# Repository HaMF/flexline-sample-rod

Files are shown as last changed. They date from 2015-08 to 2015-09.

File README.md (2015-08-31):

# Flexline sample rod

This sample rod was designed to allow magnetic resonance experiments and simulateneous measurements in a Bruker flexline MD5 resonator hold inside of a Oxford CF395 flow cryostat. Included are 3d-models, drawings, PCB layouts and production recommendations as well as part lists of stock ISO KF parts.

All in all the holder works quite nicely. It positions the sample quite accurately in the cavity's center, is leak tight, does not show performance degradation or extraordinary large heat conductions at low temperatures (liquid Helium). Empty cavity measurements vs. sample holder in cavity measurements have been performed and will be added here for reference when the results are polished. A gear can be fitted to the top rod and the whole rod can be rotated automatically (http://hannes.maier-flaig.de/goniometer/)

**Please note:** Initial design documents were in German and some elements will probably have slipped through when translating to english (read: _all_ drawings). Units are exclusively metric. 
**Licence:** The holder design is licensed under the CERN Open Hardware License v1.2. 3D models of of-shelf ISO-KF flange parts (as available from the vendors web site) are included in the project and do not fall under the license (CERN OHL v1.2) of the whole project. Copyright as far as applicable remains with the manufacturer (see below).

## Pictures and performance

The full construction as autodesk project can be found in the subfolder ./1-autodesk project/ . Drawings are also exported
to PDF in the ./2-drawings folder. Here follows a description of the parts and description of the PCB holders:

### Top
Standard ISO-KF flanges are used. Conical reduction piece [Fig. ... (2)] is beneficial because it has more space to fit the connector.
Connecting the DC lines to a breakout box is performed using lemo connectors.

### V2A rod
To the lower KF16 KF a V2A rod is welded (i.e. hard soldered).

### Sample holder support
The sample rod is designed so that Bruker holder for standard quartz glass sample tubes also fit.
In this case an extension [Fig. ... (1)] has to be used that fits the plug of the DC lines.

Shown in [Fig. ... (2) and Fig ...] is the sample holder support for PCB sample holders.

## PCB sample holders
The PCB design in ./3-PCB/PCB.brd and ./3-PCB/PCB.pdf includes three layers: Dimensions, Holes, and Top (Copper)).
It was produced on FR4 IT158 (Tg155) 1mm thickness with a cooper only plating of 35µm. All of that is pretty standard
With the supplier "Hofmann Leiterplatten" production was fast and troublefree. After tax cost was roughly 190€ per 50pcs.

 + Soldering PCBs using a hotplate and soldering paste works quite nicely. Trim pins that stick out to the backside first.
 + When breaking PCB free from full plate, length dimensions are slightly too long thus the PCBs need to be shortened. (See below)

## Empty cavity vs loaded cavity measurements

Will follow.

# Part list

| Part # | Manufacturer          | Model               | Description                                                                        |
|--------|-----------------------|---------------------|------------------------------------------------------------------------------------|
| 1      | Lemo                  | HGP.1S.306.CLLSV    | 6-pin vacuum tight receptangle                                                     |
| 2      | Pfeiffer Vacuum       |                     | ISO KF-40 blind flange (Al)                                                        |
| 3      | Pfeiffer Vacuum       |                     | ISO KF-40 centering ring and o-ring                                                |
| 4      | Pfeiffer Vacuum       |                     | ISO KF-40-16 conical reduction (Al)                                                |
| 5      | Pfeiffer Vacuum       |                     | ISO KF-16 centering ring and o-ring                                                |
| 6      | Pfeiffer Vacuum       |                     | ISO KF-16 blind flange (Al)                                                        |
| 7      |                       |                     | V2A tube, 8mm OD, 7mm ID                                                           |
| 8      |                       |                     | PEEK-1000 rod, 10mm OD                                                             |
| 9      | W+P Products          | 605-006-1-2-00      | Plug 1.27mm grid, 2 rows each 3 pins at Conrad electronics: 739179-05              |
| 10     | W+P Products          | 712-1-006-2-10-00   | Plug 1.27mm grid, 2 rows each 3 pins, right angle at Conrad electronics: 718818-05 |
| 11     | Hofmann Leiterplatten |                     | PCB sample holder, see below                                                       |
| 12     | Lemo                  | 060080              | Cable for in-road as well as to breakout box                                       |
| 13     | Lemo                  | FFA.1S.306.CLAC52ZN | Plug, straight for breakout box. 2 times                                           |
| 14     | Lemo                  | ERA.1S.306.CLL      | Receptangle for breakout box                                                       |
| 15     | Telegärtner           | J01001A0043         | Isolating BNC female, straight for breakout box                                    |

## Remarks on parts, design considerations
 +  Sample side plug and jack are not polarity proof. This would be possible e.g. with Omnetics miniature plugs. 
    These are, however too expensive for this type of application and are not justified by just being polarity proof

# Further plans (and decisions that turned out not to be so clever)

 + Even though there are 6 DC lines, the PCBs connect only 5 into the cavity. Six leads would fit on the PCB just as well. 
   In case very low loading of the cavity is needed, only two leads should be used in any case.
 + PCB with 1.27x2.54mm² grid dimensions use 1.27x1.27mm² in next iterations. Rod-side is already the later gridsize.
 + PCB tolerance when breaking free instead of milling has been choosen too small. PCBs should be 0.5mm shorter in next iteration

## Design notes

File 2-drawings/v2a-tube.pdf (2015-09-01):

1

A4

Probenstab

## Edelstahl

Status | |nderungen | DATUM | Name

Gezeichnet

Kontrolliert

Norm

DATUM | Name
04.09.2014 | Hannes Maier-Flaig

4

4

0,0

0

P8,00 | P7,00 DURCH M7x0.5 - 6H
| INSIDE THREAD; min. 12 deep

Weld/Hard solder to KF16 Blindflansch

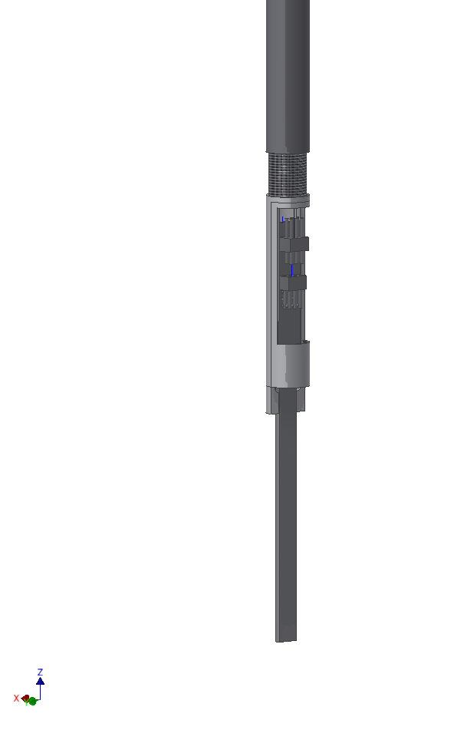
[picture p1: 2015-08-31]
0-images/bottom-pcb-holder.png

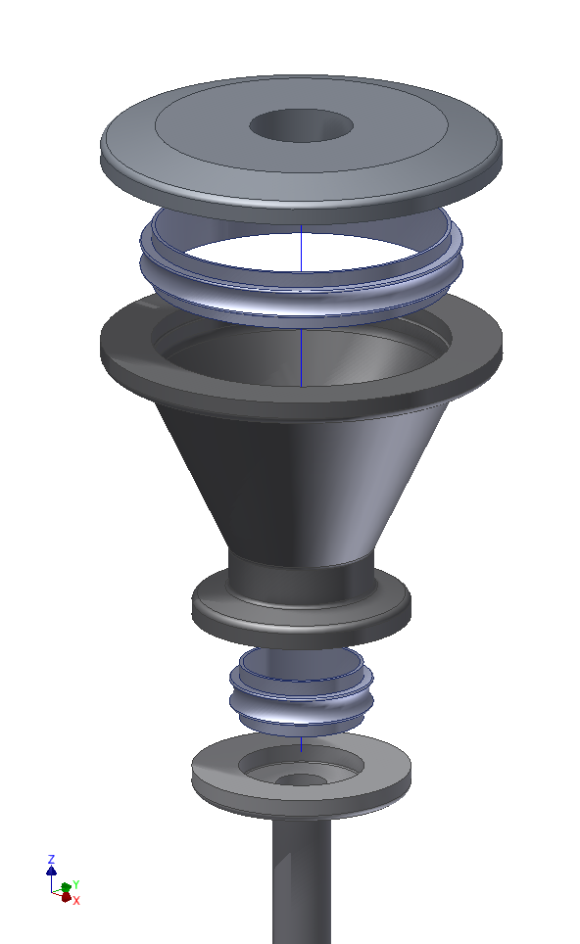
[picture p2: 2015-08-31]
0-images/top-flanges.png

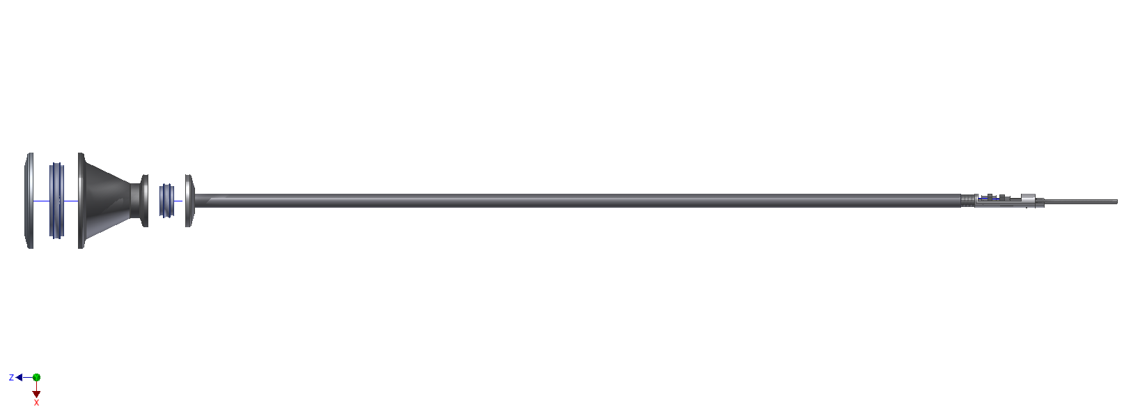
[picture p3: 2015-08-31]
0-images/total.png

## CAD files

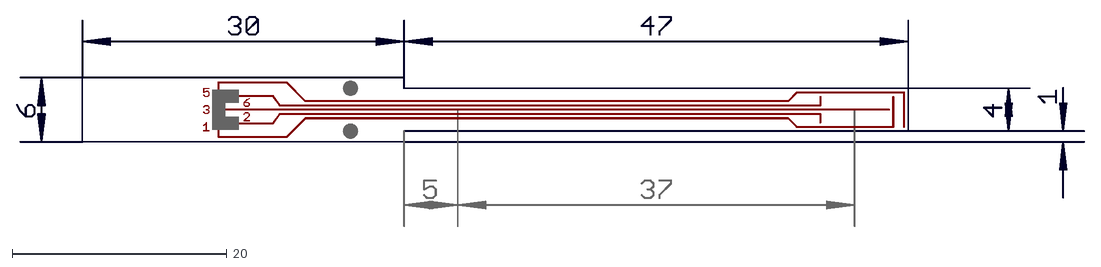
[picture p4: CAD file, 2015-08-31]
3-PCBs/PCB.dxf
99.6 x 19.6

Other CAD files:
1-autodesk project/drawings/PEEK-extension.dwg
1-autodesk project/drawings/KF16BF.dwg
1-autodesk project/drawings/KF40BF.dwg
1-autodesk project/drawings/v2a-tube.dwg
1-autodesk project/Importierte Komponenten/110FBL016/110FBL016.ipt
1-autodesk project/Importierte Komponenten/110FBL016/OldVersions/110FBL016.0002.ipt
1-autodesk project/Importierte Komponenten/110FBL016/OldVersions/110FBL016.0003.ipt
1-autodesk project/Importierte Komponenten/110FBL040/110FBL040.ipt
1-autodesk project/Importierte Komponenten/110FBL040/OldVersions/110FBL040.0001.ipt
1-autodesk project/Importierte Komponenten/110FBL040/OldVersions/110FBL040.0004.ipt
1-autodesk project/Importierte Komponenten/116ZRG016/116ZRG016.ipt
1-autodesk project/Importierte Komponenten/116ZRG016/OldVersions/116ZRG016.0002.ipt
1-autodesk project/Importierte Komponenten/116ZRG040/116ZRG040.ipt
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

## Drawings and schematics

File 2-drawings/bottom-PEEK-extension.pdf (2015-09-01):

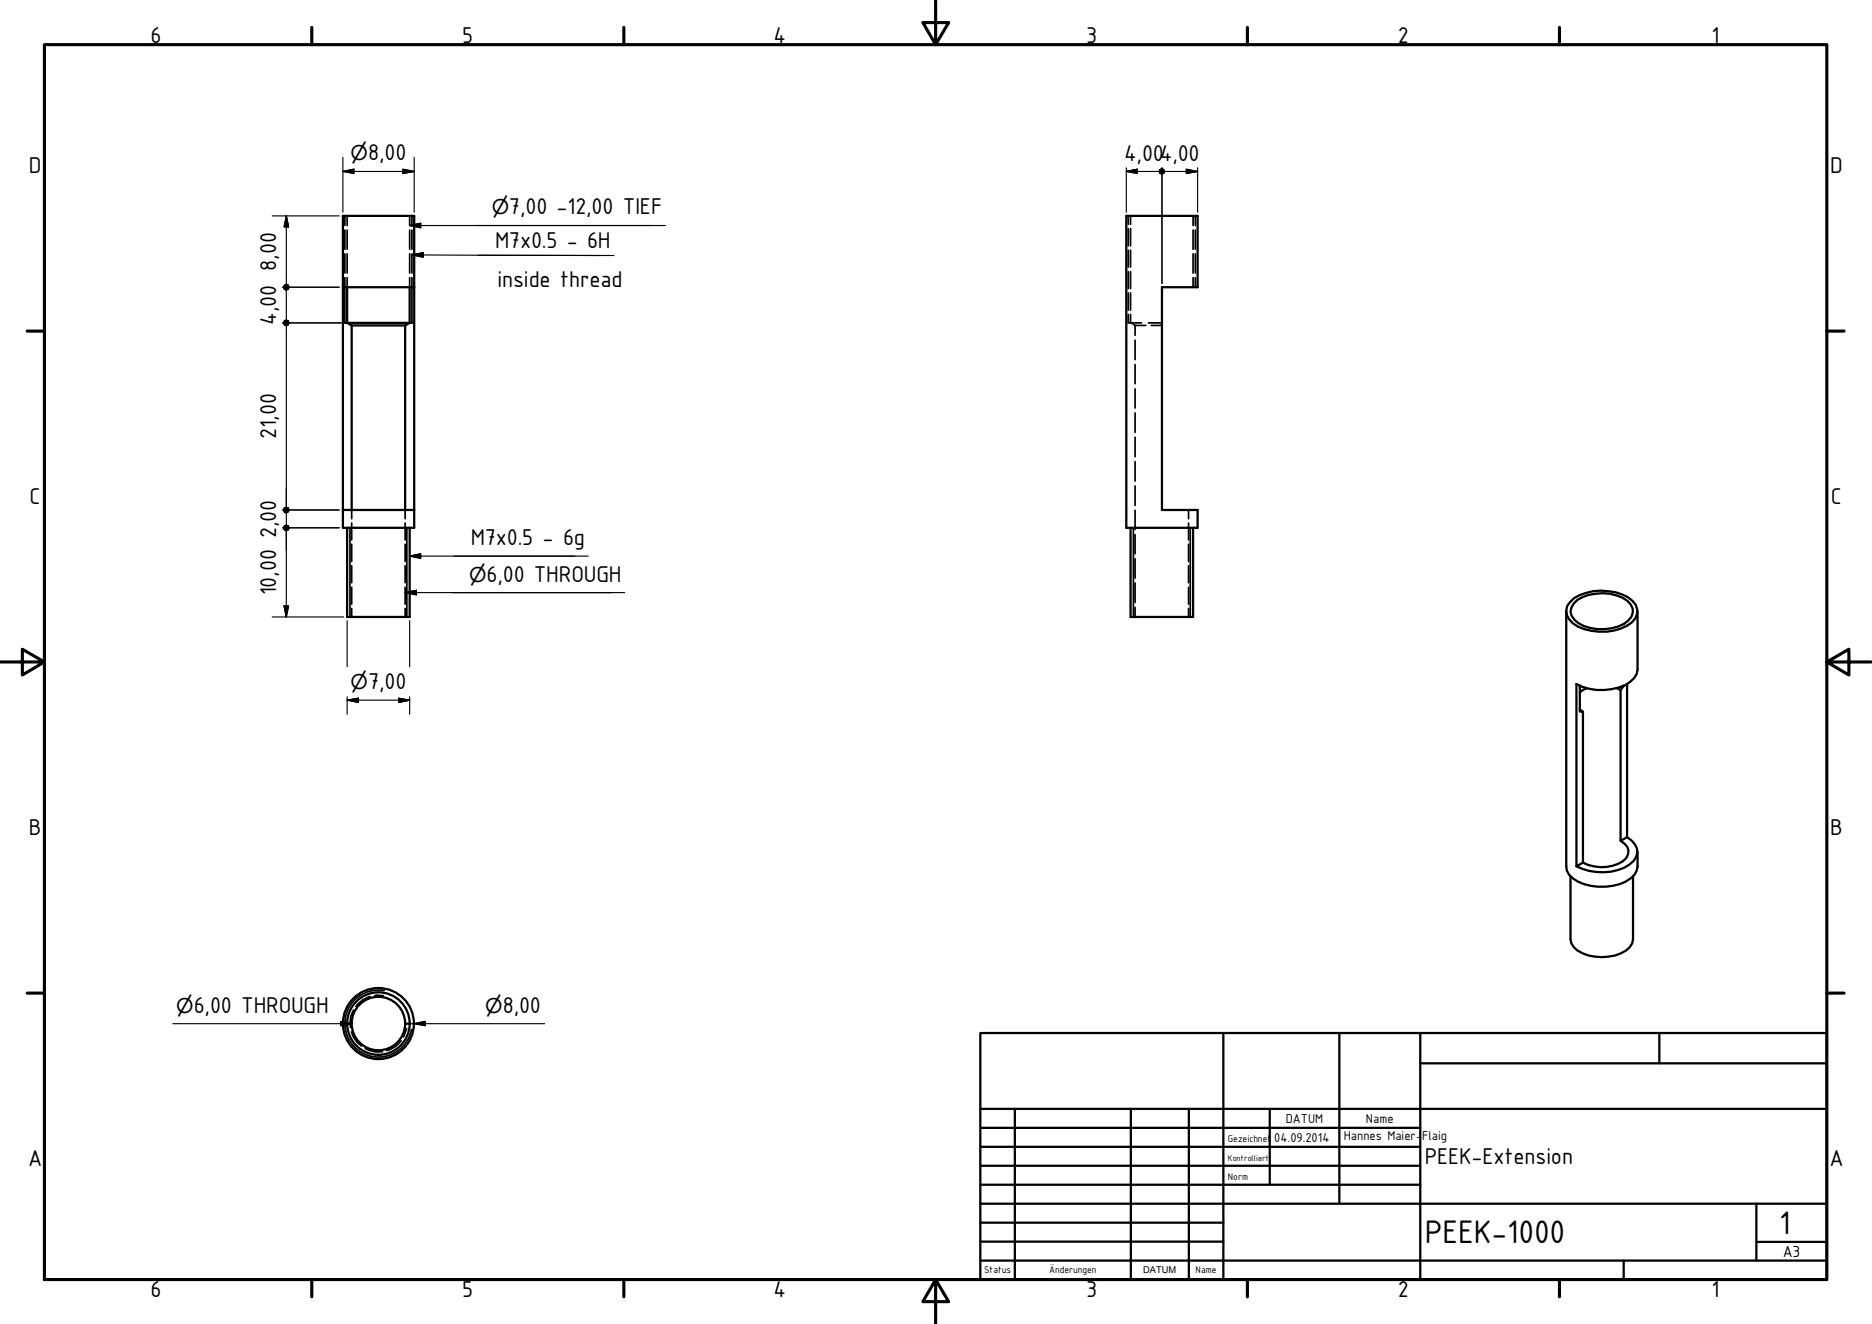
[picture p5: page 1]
PEEK-Extension; PEEK-1000; Status; |nderungen; DATUM; Name; Gezeichnet; Kontrolliert; Norm; Hannes Maier-Flaig; M7x0.5 - 6g P6,00 THROUGH; P7,00 -12,00 TIEF; P6,00 THROUGH; inside thread

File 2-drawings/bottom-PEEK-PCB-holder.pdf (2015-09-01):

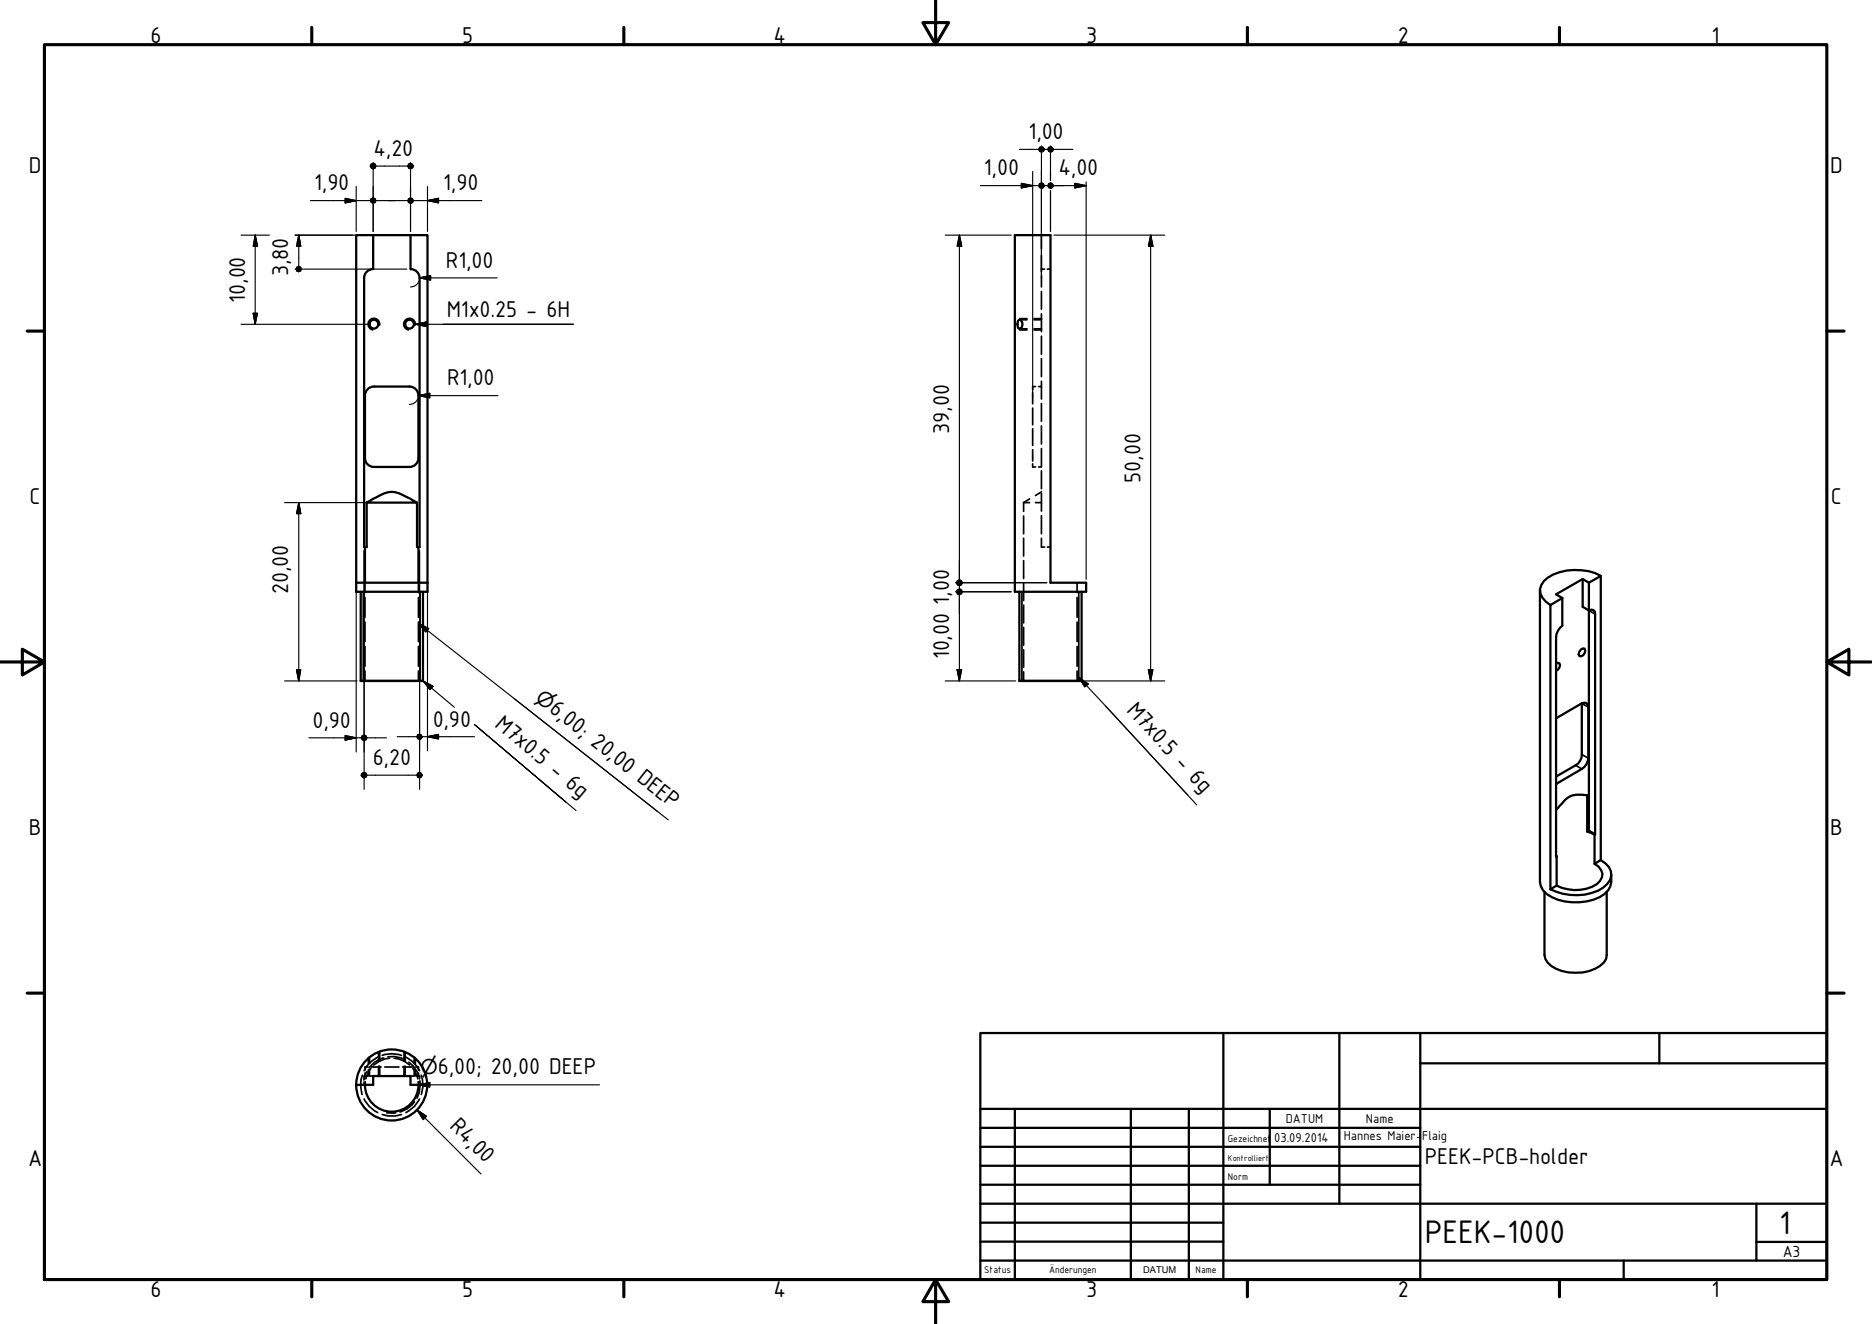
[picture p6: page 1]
PEEK-1000; Status; |nderungen; DATUM; Name; Gezeichnet; Kontrolliert; Norm; Hannes Maier-Flaig; P6,00; 20,00 DEEP

PEEK-PCB-holder

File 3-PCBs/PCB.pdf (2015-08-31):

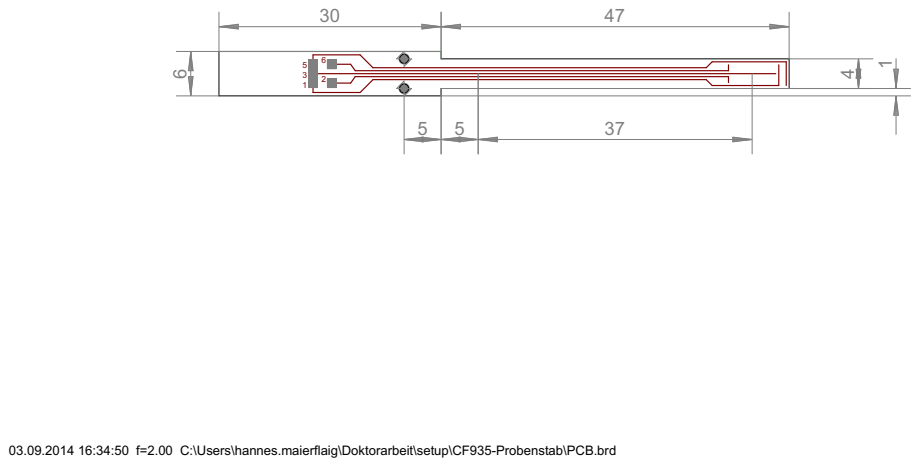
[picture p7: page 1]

03.09.2014 16:34:50 f=2.00 C:\Users\hannes.maierflaig\Doktorarbeit\setup\CF935-Probenstab\PCB.brd

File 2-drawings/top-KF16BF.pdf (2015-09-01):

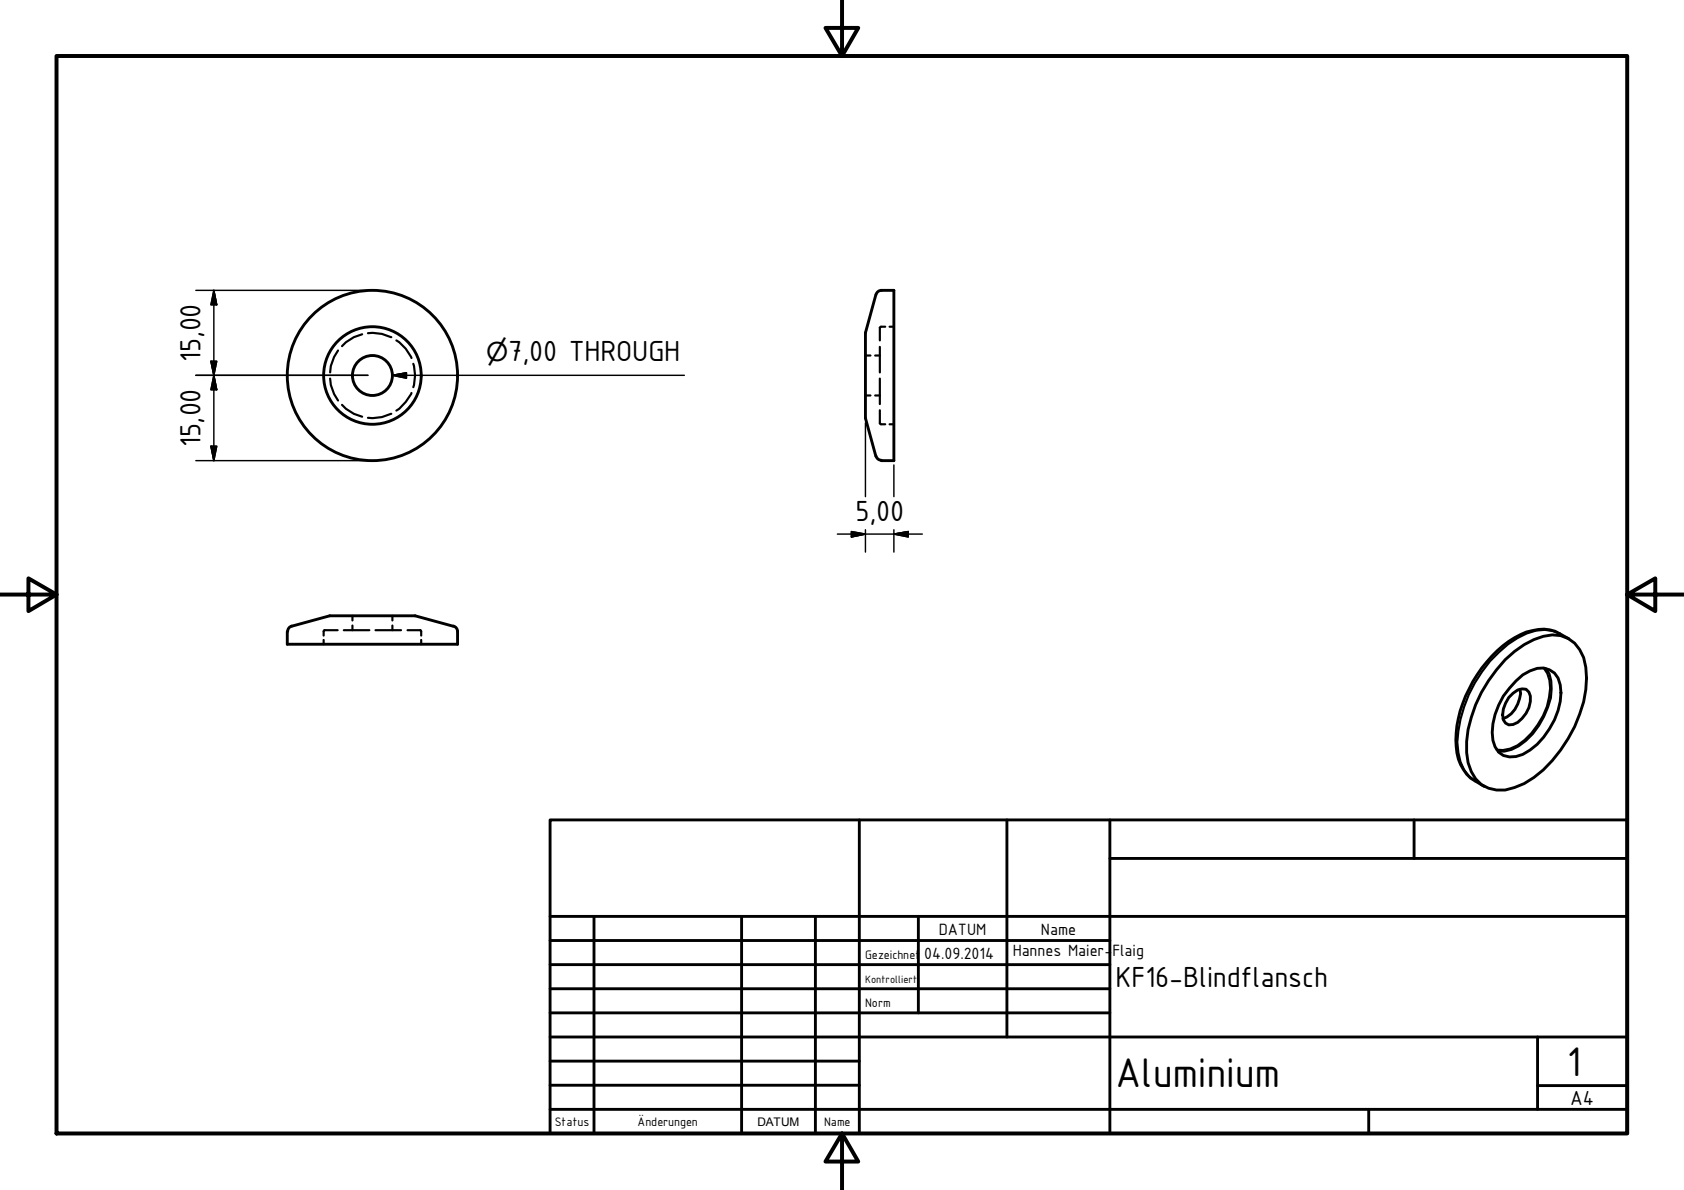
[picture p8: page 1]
KF16-Blindflansch; Aluminium; Status; |nderungen; DATUM; Name; Gezeichnet; Kontrolliert; Norm; Hannes Maier-Flaig; P7,00 THROUGH

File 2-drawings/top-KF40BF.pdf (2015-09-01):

# P14,20 THROUGH

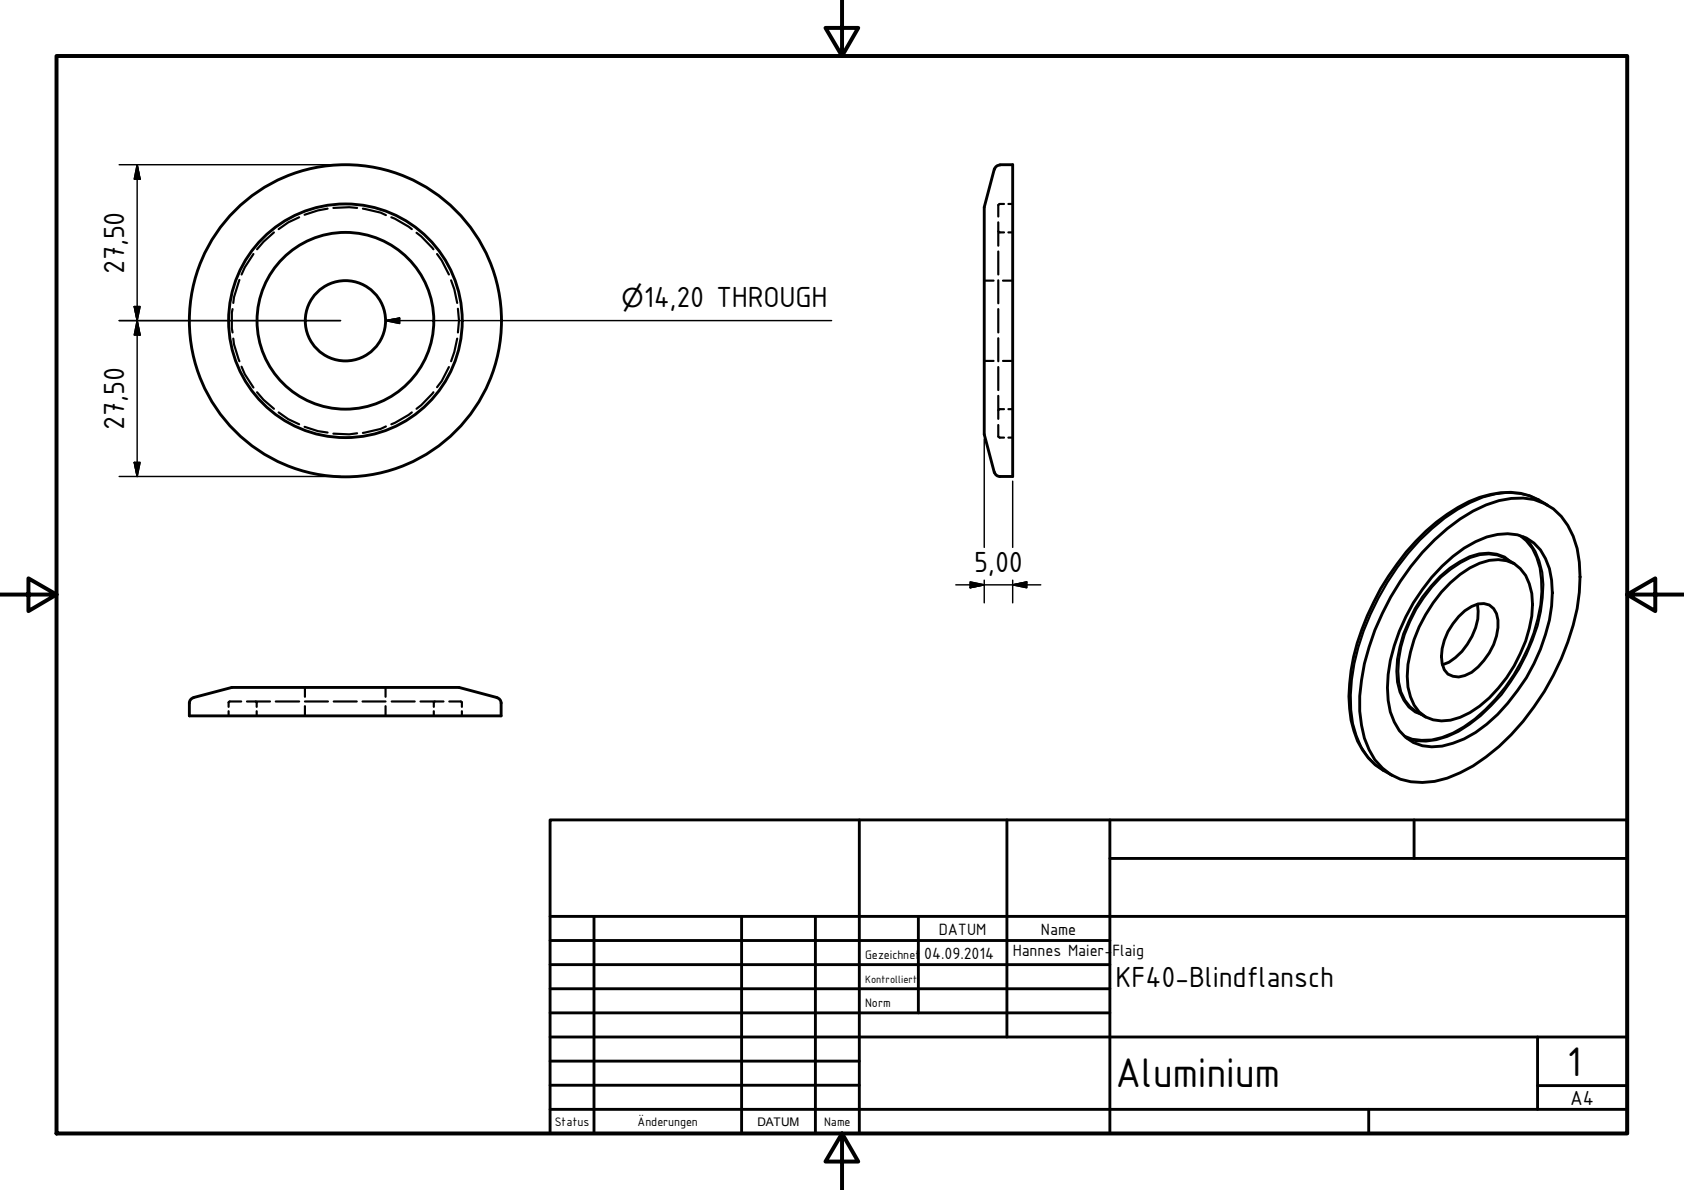
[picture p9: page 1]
KF40-Blindflansch; Aluminium; Status; |nderungen; DATUM; Name; Gezeichnet; Kontrolliert; Norm; Hannes Maier-Flaig

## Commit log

2015-08-31 first online version with readme in github markdown style. exported drawings are still missing as they are not polished yet.
    [110FBL016.0002.ipt, 110FBL016.0003.ipt, 110FBL016.ipt, 110FBL040.0001.ipt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]
2015-09-01 add pdf drawings
    [KF16BF.0003.dwg, KF16BF.dwg, KF40BF.0003.dwg, KF40BF.dwg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]
